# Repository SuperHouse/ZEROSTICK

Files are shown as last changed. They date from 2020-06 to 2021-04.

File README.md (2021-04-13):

"ZeroStick" Zero-Deflection Assistive Technology Joystick
==========================================================

ZeroStick is a joystick that uses strain gauges to measure force
applied to it, without the joystick needing to move. The joystick
"position" is determined from the force being applied to it, instead of
any physical deflection of the stick.

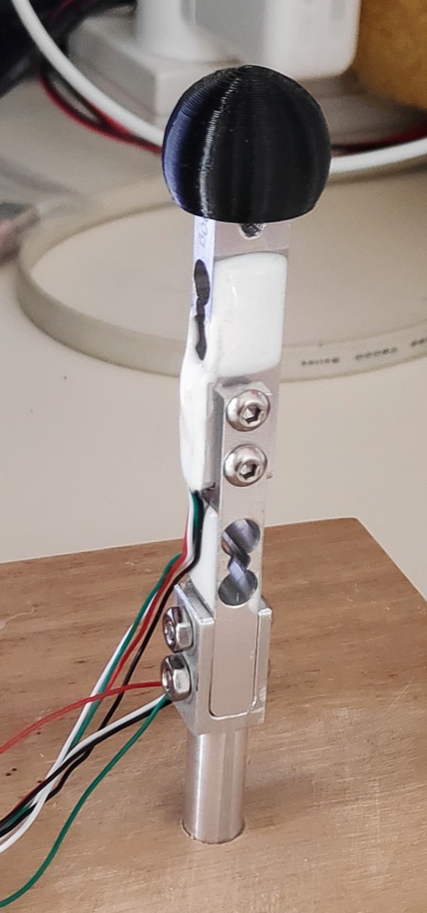
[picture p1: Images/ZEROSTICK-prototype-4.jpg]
ZeroStick Joystick


The term "position" is used here to signify the virtual position of the
joystick, even though it doesn't physically move. As more force is
applied, the virtual position of the joystick is considered to change.

This allows it to be used by people with a limited range of motion,
such as from Duchenne muscular dystrophy.

The sensitivity of the joystick can be adjusted in software by changing
the scaling of the values detected by the strain gauges.

The position value is measured as % deflection from the zero (central)
position, ie: from -100% to +100%. This is equivalent to full effort by
the user in each direction.

The force applied to the load cells is measured using a NAU7802 ADC
with an I2C interface. The input channels are split so that a single
ADC can read both the X and the Y axis load cells sequentially.

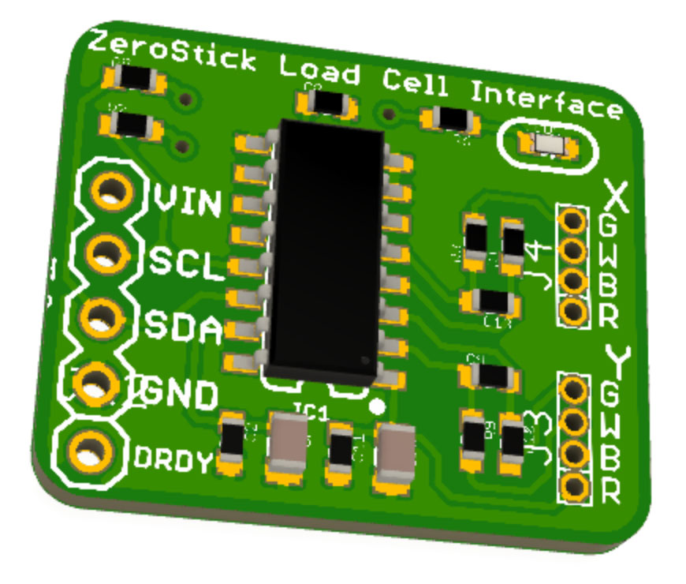
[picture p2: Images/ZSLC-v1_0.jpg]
ZeroStick Load Cell Interface PCB


You can view more details at:

  http://www.superhouse.tv/zerostick

Hardware
--------
The "Hardware" directory contains the PCB design as an EAGLE project.
EAGLE PCB design software is available from Autodesk free for
non-commercial use.

Firmware
--------
The "Firmware" directory contains example firmware as an Arduino
project.

The example firmware has three output methods:

1. Mouse output. When enabled and plugged into a computer, the ZeroStick
will emulate a USB mouse. Buttons on the ZeroStick can also send left
and right click events.

2. Joystick output. When enabled and plugged into a computer, the
ZeroStick will emulate a USB game controller with a joystick.

3. I2C digital potentiometer output. External I2C digital potentiometers
can be connected, which can then emulate a simple analog joystick
when connected to another device such as a wheelchair. This allows the
ZeroStick to control wheelchairs that expect to have a normal joystick
attached.

Credits
-------
  * Jonathan Oxer <jon@oxer.com.au>
  * Chris Fryer <chris.fryer78@gmail.com>

License
-------
Copyright 2019-2021 SuperHouse Automation Pty Ltd  www.superhouse.tv  

The hardware portion of this project is licensed under the TAPR Open
Hardware License (www.tapr.org/OHL). The "license" folder within this
repository contains a copy of this license in plain text format.

The software portion of this project is licensed under the Simplified
BSD License. The "licence" folder within this project contains a
copy of this license in plain text format.

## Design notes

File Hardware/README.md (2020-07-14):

SuperButton Assistive Technology Button
=======================================
Copyright 2020 SuperHouse Automation Pty Ltd <www.superhouse.tv>  
Designed by Jonathan Oxer

Load-cell based button that can have the required activation force
adjusted in software, to tune it based on the needs of the user.

PCB render

Features:

 * 1 x input connection for a load-cell based button
 * 1 x USB connection for power or to emulate an input device
 * 1 x switched output (either N.O. or N.C.) to control other devices
 * 128x32 OLED to show current force reading and activation threshold
 * Rotary encoder to adjust activation threshold
 * "Tare" button to reset zero point
 * Pulse stretching feature controlled by slide switch

More information is available at:

  http://www.superhouse.tv/sb

INSTALLATION
------------
The design is saved as an EAGLE project. EAGLE PCB design software is
available from www.cadsoftusa.com free for non-commercial use. To use
this project download it and place the directory containing these files
into the "eagle" directory on your computer. Then open EAGLE and
navigate to the project.

DISTRIBUTION
------------
The specific terms of distribution of this project are governed by the
license referenced below.

LICENSE
-------
Licensed under the TAPR Open Hardware License (www.tapr.org/OHL).
The "license" folder within this repository also contains a copy of
this license in plain text format.

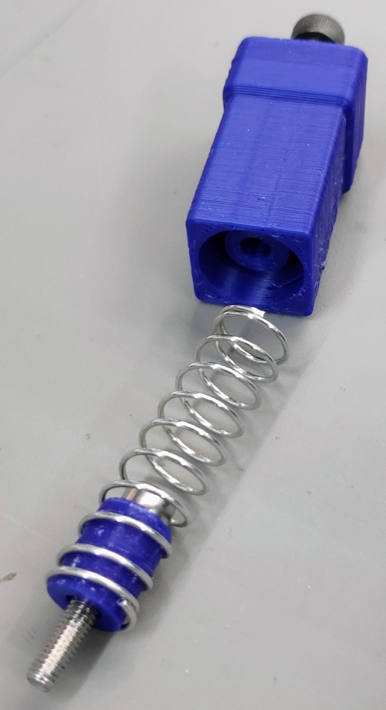
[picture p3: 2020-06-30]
Images/2020-01-04 17.47.43.jpg

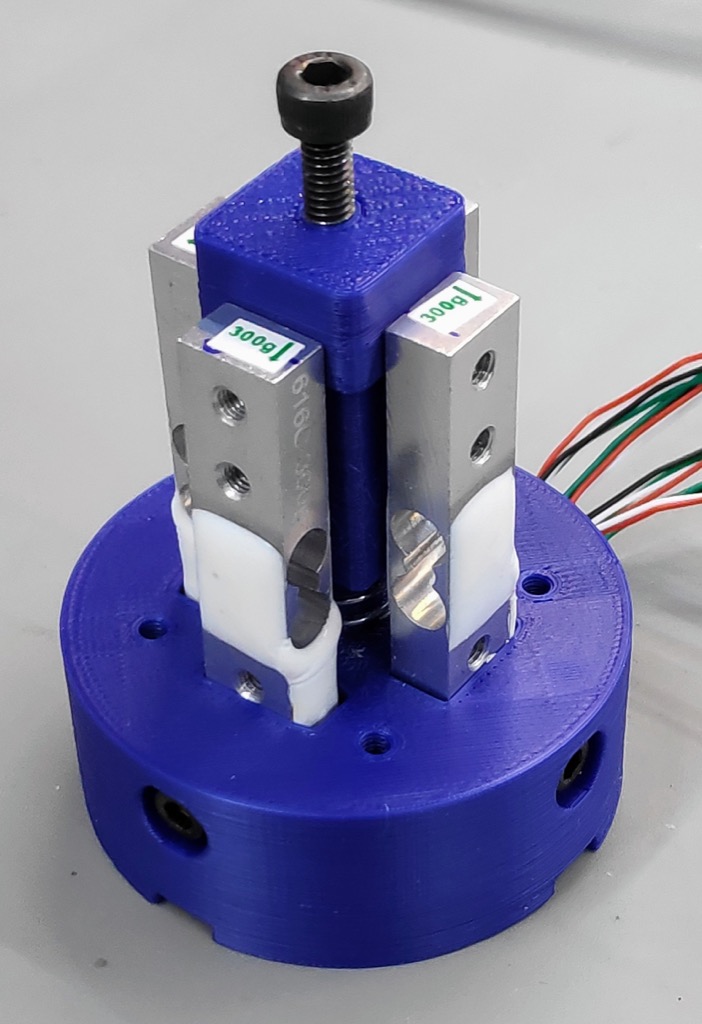
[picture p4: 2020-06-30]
Images/2020-01-04 17.36.29.jpg

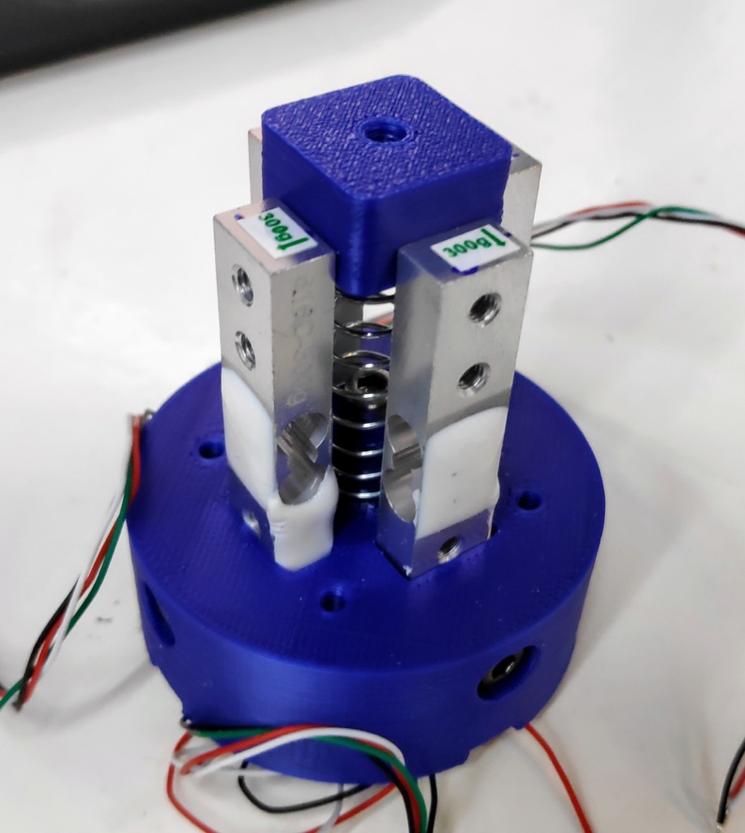
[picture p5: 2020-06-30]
Images/2020-01-04 15.48.38.jpg

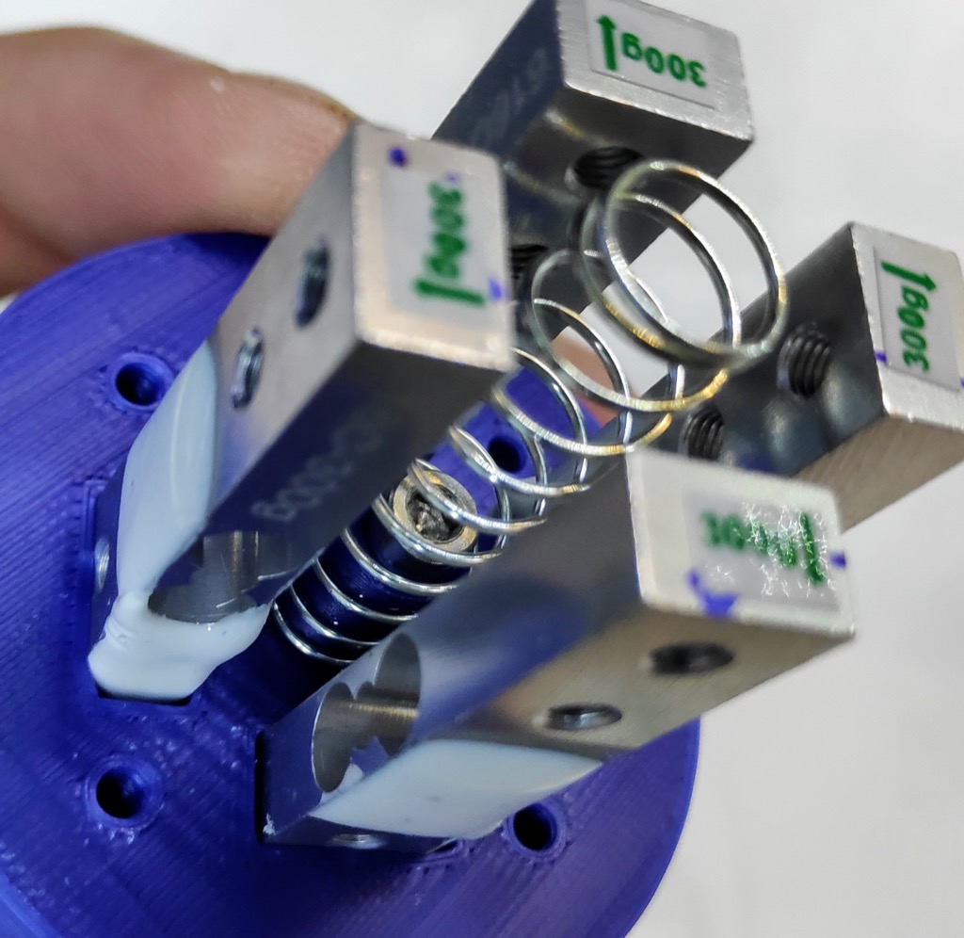
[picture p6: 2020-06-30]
Images/2020-01-04 14.36.33.jpg

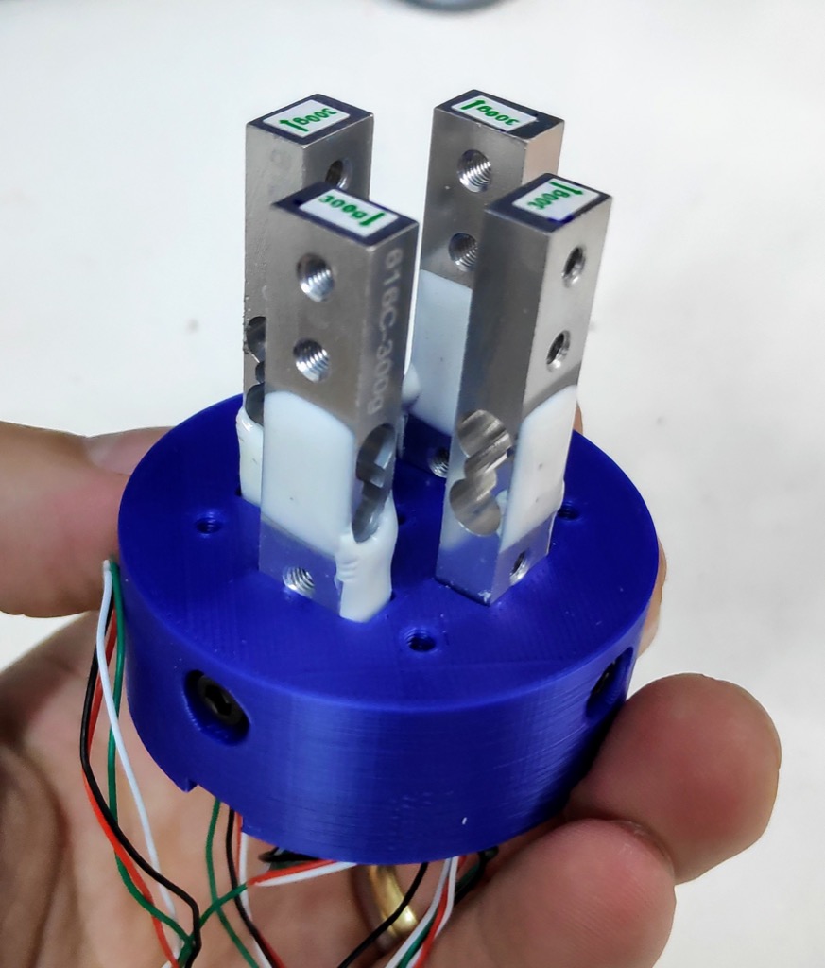
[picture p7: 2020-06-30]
Images/2020-01-04 13.35.04.jpg

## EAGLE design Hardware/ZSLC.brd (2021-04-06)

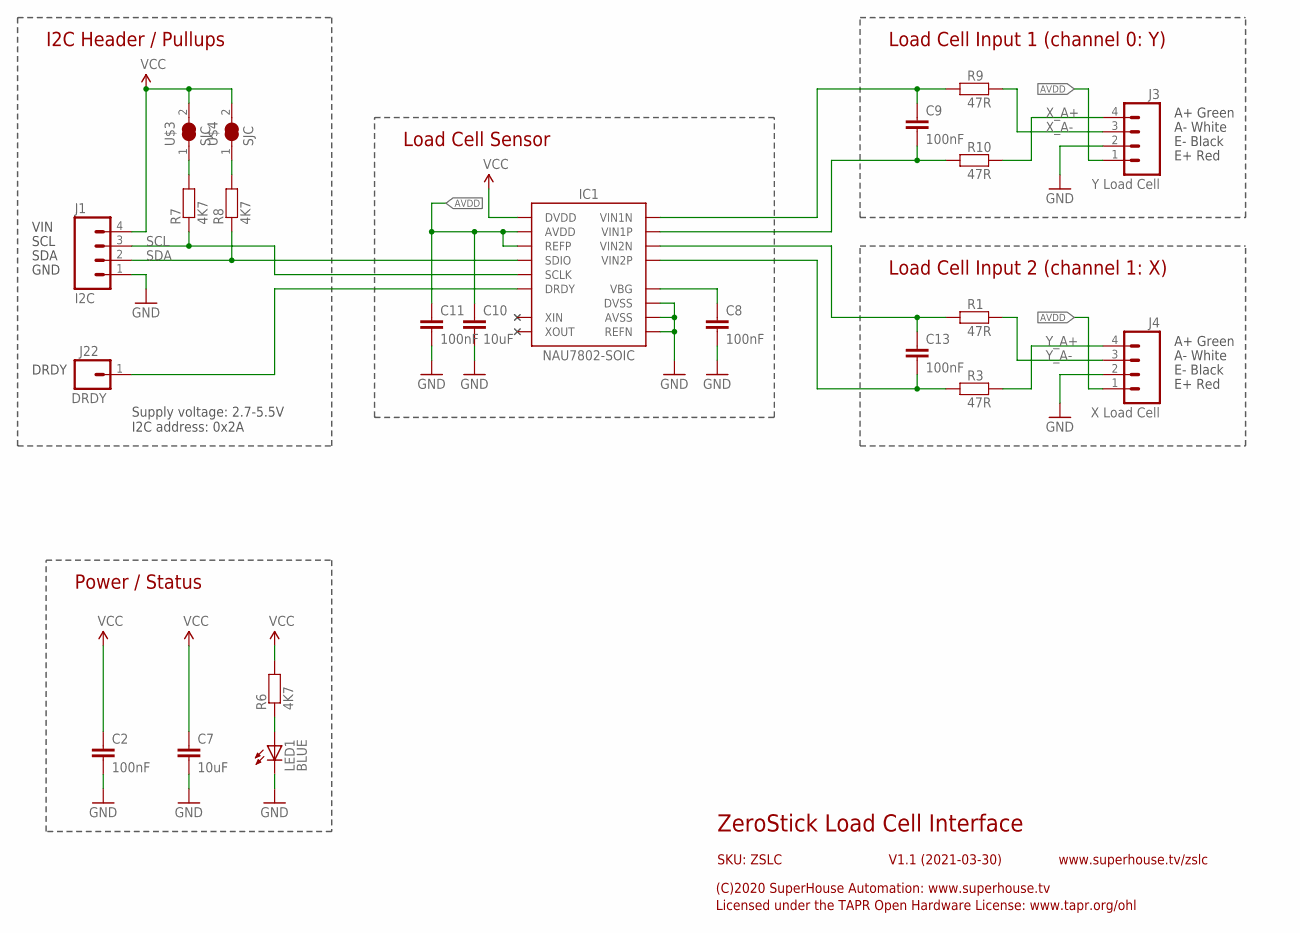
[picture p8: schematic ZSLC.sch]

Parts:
C2, C8, C9, C11, C13: 100nF; C0603
C7, C10: 10uF; C0805
IC1: NAU7802-SOIC; SO16
J1: I2C; 1X04
J3: Y Load Cell; 1X04-1.27-PLAIN
J4: X Load Cell; 1X04-1.27-PLAIN
J22: DRDY; 1X01
LED1: BLUE; LED-0603
R1, R3, R9, R10: 47R; R0603
R6, R7, R8: 4K7; R0603
U$3, U$4: SJC

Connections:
AVDD: C10.1, C11.1, IC1.1 (REFP), IC1.16 (AVDD), J3.1, J4.1
GND: C2.2, C7.2, C8.2, C10.2, C11.2, IC1.7 (REFN), IC1.8 (AVSS), IC1.9 (DVSS), J1.1, J3.2, J4.2, LED1.C
unnamed: IC1.12 (DRDY), J22.1
unnamed: C13.1, IC1.4 (VIN2N), R1.1
unnamed: C13.2, IC1.5 (VIN2P), R3.1
unnamed: LED1.A, R6.1
unnamed: C9.1, IC1.2 (VIN1N), R9.1
unnamed: C9.2, IC1.3 (VIN1P), R10.1
unnamed: C8.1, IC1.6 (VBG)
unnamed: R7.2, U$3.1
unnamed: R8.2, U$4.1
SCL: IC1.13 (SCLK), J1.3, R7.1
SDA: IC1.14 (SDIO), J1.2, R8.1
VCC: C2.1, C7.1, IC1.15 (DVDD), J1.4, R6.2, U$3.2, U$4.2
X_A+: J3.4, R10.2
X_A-: J3.3, R9.2
Y_A+: J4.4, R3.2
Y_A-: J4.3, R1.2

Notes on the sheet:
ZeroStick Load Cell Interface
V1.1 (2021-03-30)
SKU: ZSLC
(C)2020 SuperHouse Automation: www.superhouse.tv
Licensed under the TAPR Open Hardware License: www.tapr.org/ohl
www.superhouse.tv/zslc
Power / Status
Load Cell Input 1 (channel 0: Y)
Load Cell Input 2 (channel 1: X)
I2C Header / Pullups
E+ Red
E- Black
A- White
A+ Green
Supply voltage: 2.7-5.5V I2C address: 0x2A
Load Cell Sensor
VIN
SCL
SDA
GND
DRDY

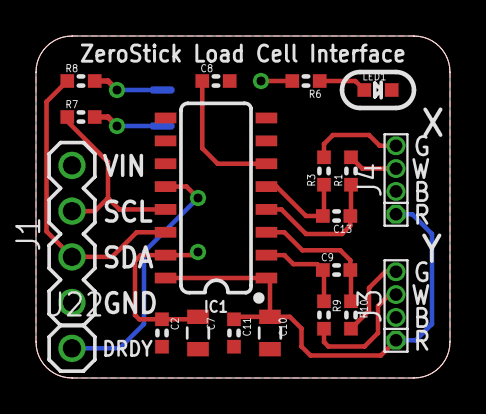
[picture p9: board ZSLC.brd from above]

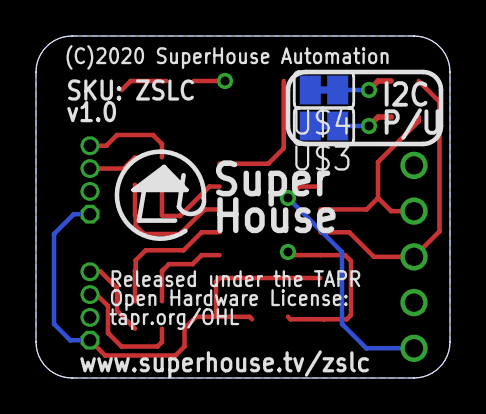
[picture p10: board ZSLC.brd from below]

Board: 2 copper layers, 23.0 x 19.0 mm, 22 parts (2 on the bottom side), 18 nets.

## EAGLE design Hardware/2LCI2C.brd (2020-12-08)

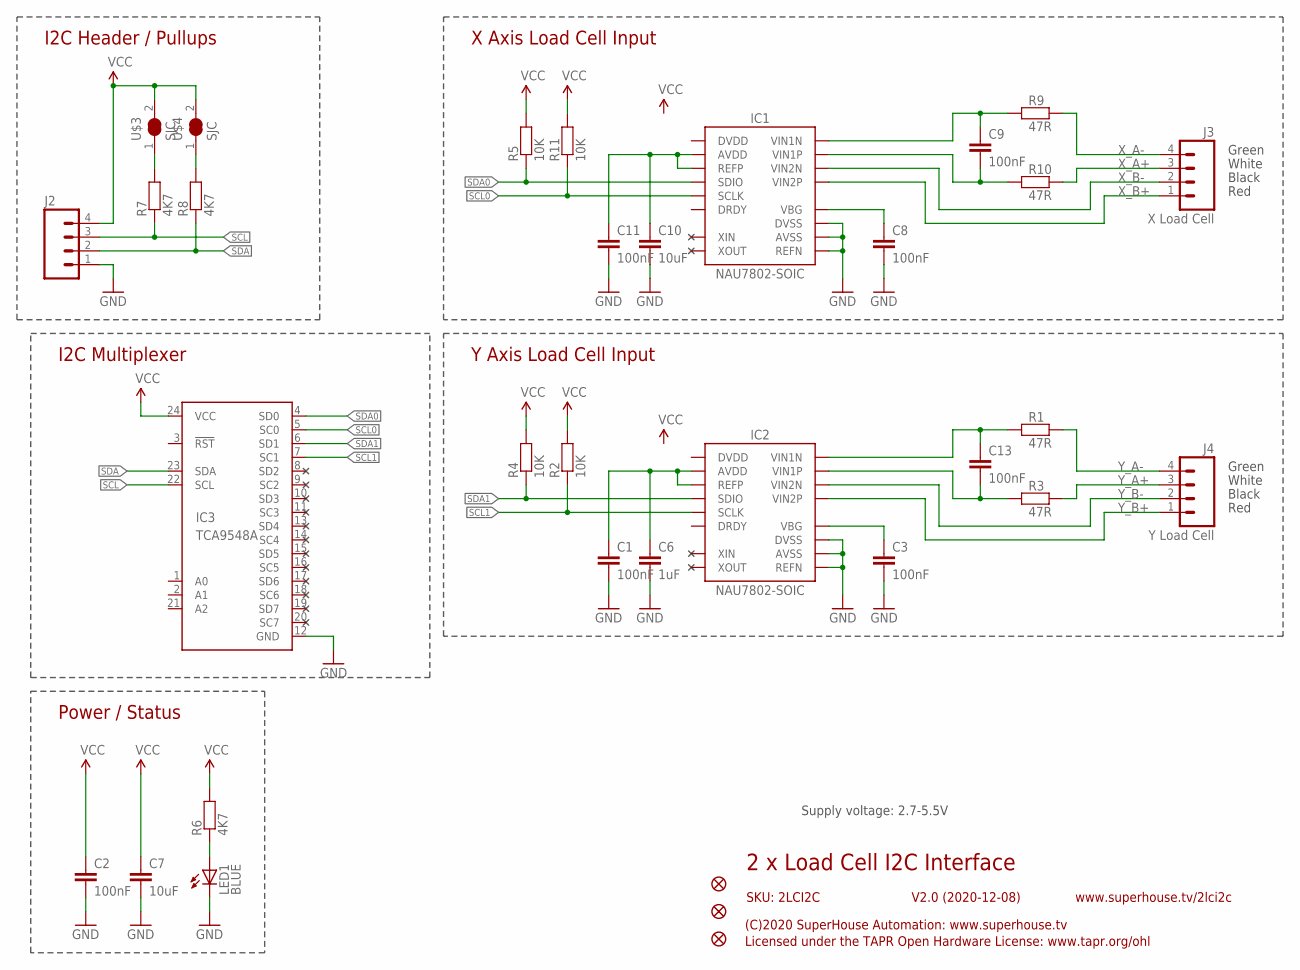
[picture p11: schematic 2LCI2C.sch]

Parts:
C1, C2, C3, C8, C9, C11, C13: 100nF; C0603
C6: 1uF; C0805
C7, C10: 10uF; C0805
IC1, IC2: NAU7802-SOIC; SO16
IC3: TCA9548A; TSSOP24
J2: M04-PLAIN; 1X04
J3: X Load Cell; 1X04-1.27-PLAIN
J4: Y Load Cell; 1X04-1.27-PLAIN
LED1: BLUE; LED-0603
R1, R3, R9, R10: 47R; R0603
R2, R4, R5, R11: 10K; R0603
R6, R7, R8: 4K7; R0603
U$3, U$4: SJC
U$5, U$10, U$11: FIDUCIAL1X2.5; FIDUCIAL-1X2.5

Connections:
GND: C1.2, C2.2, C3.2, C6.2, C7.2, C8.2, C10.2, C11.2, IC1.7 (REFN), IC1.8 (AVSS), IC1.9 (DVSS), IC2.7 (REFN), IC2.8 (AVSS), IC2.9 (DVSS), IC3.12 (GND), J2.1, LED1.C
unnamed: C3.1, IC2.6 (VBG)
unnamed: C13.1, IC2.2 (VIN1N), R1.1
unnamed: C1.1, C6.1, IC2.1 (REFP), IC2.16 (AVDD)
unnamed: C13.2, IC2.3 (VIN1P), R3.1
unnamed: LED1.A, R6.1
unnamed: C9.1, IC1.2 (VIN1N), R9.1
unnamed: C9.2, IC1.3 (VIN1P), R10.1
unnamed: C8.1, IC1.6 (VBG)
unnamed: C10.1, C11.1, IC1.1 (REFP), IC1.16 (AVDD)
unnamed: R7.2, U$3.1
unnamed: R8.2, U$4.1
SCL: IC3.22 (SCL), J2.3, R7.1
SCL0: IC1.13 (SCLK), IC3.5 (SC0), R11.1
SCL1: IC2.13 (SCLK), IC3.7 (SC1), R2.1
SDA: IC3.23 (SDA), J2.2, R8.1
SDA0: IC1.14 (SDIO), IC3.4 (SD0), R5.1
SDA1: IC2.14 (SDIO), IC3.6 (SD1), R4.1
VCC: C2.1, C7.1, IC3.24 (VCC), J2.4, R2.2, R4.2, R5.2, R6.2, R11.2, U$3.2, U$4.2
X_A+: J3.3, R10.2
X_A-: J3.4, R9.2
X_B+: IC1.5 (VIN2P), J3.1
X_B-: IC1.4 (VIN2N), J3.2
Y_A+: J4.3, R3.2
Y_A-: J4.4, R1.2
Y_B+: IC2.5 (VIN2P), J4.1
Y_B-: IC2.4 (VIN2N), J4.2

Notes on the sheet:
2 x Load Cell I2C Interface
V2.0 (2020-12-08)
SKU: 2LCI2C
(C)2020 SuperHouse Automation: www.superhouse.tv
Licensed under the TAPR Open Hardware License: www.tapr.org/ohl
www.superhouse.tv/2lci2c
Power / Status
X Axis Load Cell Input
Y Axis Load Cell Input
I2C Header / Pullups
I2C Multiplexer
Red
Black
White
Green
Supply voltage: 2.7-5.5V

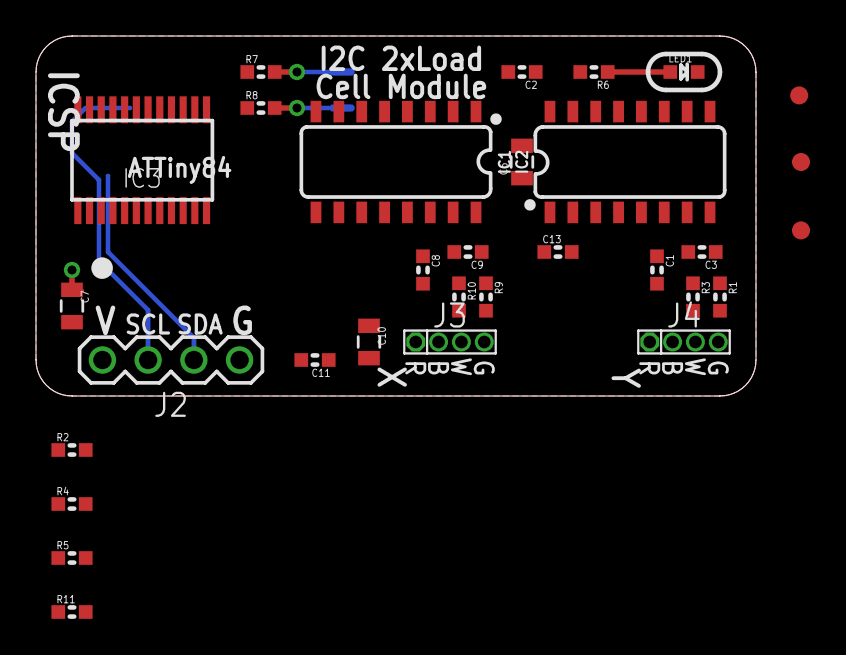
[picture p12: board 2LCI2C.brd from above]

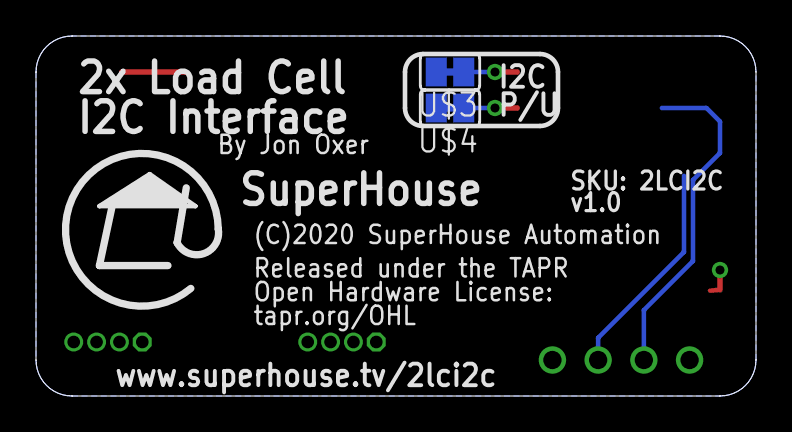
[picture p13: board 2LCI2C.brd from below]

Board: 2 copper layers, 40.0 x 20.0 mm, 33 parts (2 on the bottom side), 27 nets.

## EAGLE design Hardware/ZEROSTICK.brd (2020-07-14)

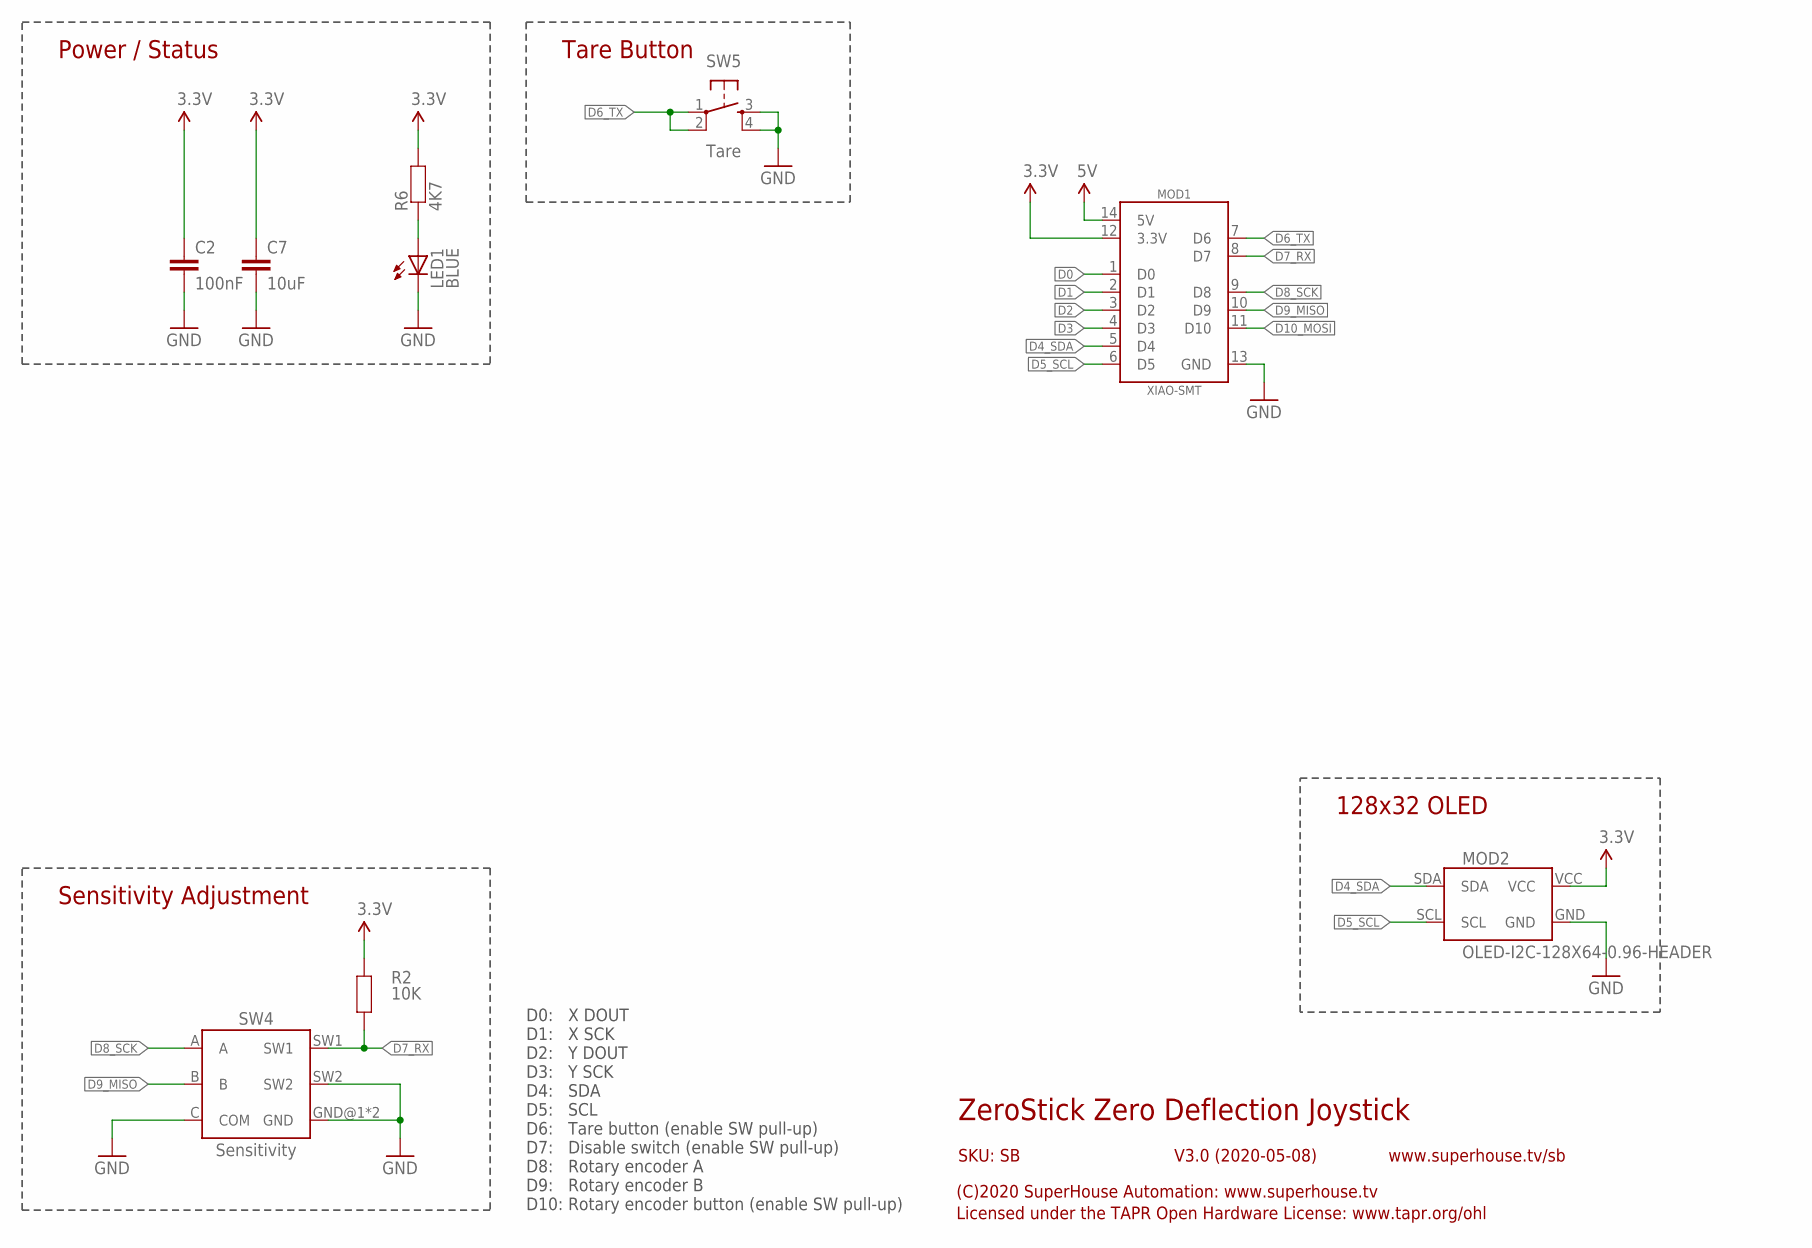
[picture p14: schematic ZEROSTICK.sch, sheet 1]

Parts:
C2: 100nF; C0603
C7: 10uF; C0805
LED1: BLUE; LED-0603
MOD1: XIAO-SMT
MOD2: OLED-I2C-128X64-0.96-HEADER; OLED-128X64-0.96-HEADER
R2: 10K; R0603
R6: 4K7; R0603
SW4: Sensitivity; PEC12R
SW5: Tare; TACTILE-PTH-4.5MM

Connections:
3.3V: C2.1, C7.1, MOD1.12 (3.3V), MOD2.VCC, R2.2, R6.2; also elsewhere on the board
5V: MOD1.14 (5V)
D0: MOD1.1 (D0); also elsewhere on the board
D1: MOD1.2 (D1); also elsewhere on the board
D2: MOD1.3 (D2); also elsewhere on the board
D3: MOD1.4 (D3); also elsewhere on the board
D4_SDA: MOD1.5 (D4), MOD2.SDA
D5_SCL: MOD1.6 (D5), MOD2.SCL
D6_TX: MOD1.7 (D6), SW5.1, SW5.2
D7_RX: MOD1.8 (D7), R2.1, SW4.SW1
D8_SCK: MOD1.9 (D8), SW4.A
D9_MISO: MOD1.10 (D9), SW4.B
D10_MOSI: MOD1.11 (D10)
GND: C2.2, C7.2, LED1.C, MOD1.13 (GND), MOD2.GND, SW4.C (COM), SW4.GND@1 (GND), SW4.GND@2 (GND), SW4.SW2, SW5.3, SW5.4; also elsewhere on the board
unnamed: LED1.A, R6.1

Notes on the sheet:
Tare Button
ZeroStick Zero Deflection Joystick
V3.0 (2020-05-08)
SKU: SB
(C)2020 SuperHouse Automation: www.superhouse.tv
Licensed under the TAPR Open Hardware License: www.tapr.org/ohl
www.superhouse.tv/sb
Power / Status
Sensitivity Adjustment
128x32 OLED
D0: X DOUT D1: X SCK D2: Y DOUT D3: Y SCK D4: SDA D5: SCL D6: Tare button (enable SW pull-up) D7: Disable switch (enable SW pull-up) D8: Rotary encoder A D9: Rotary encoder B D10: Rotary encoder button (enable SW pull-up)

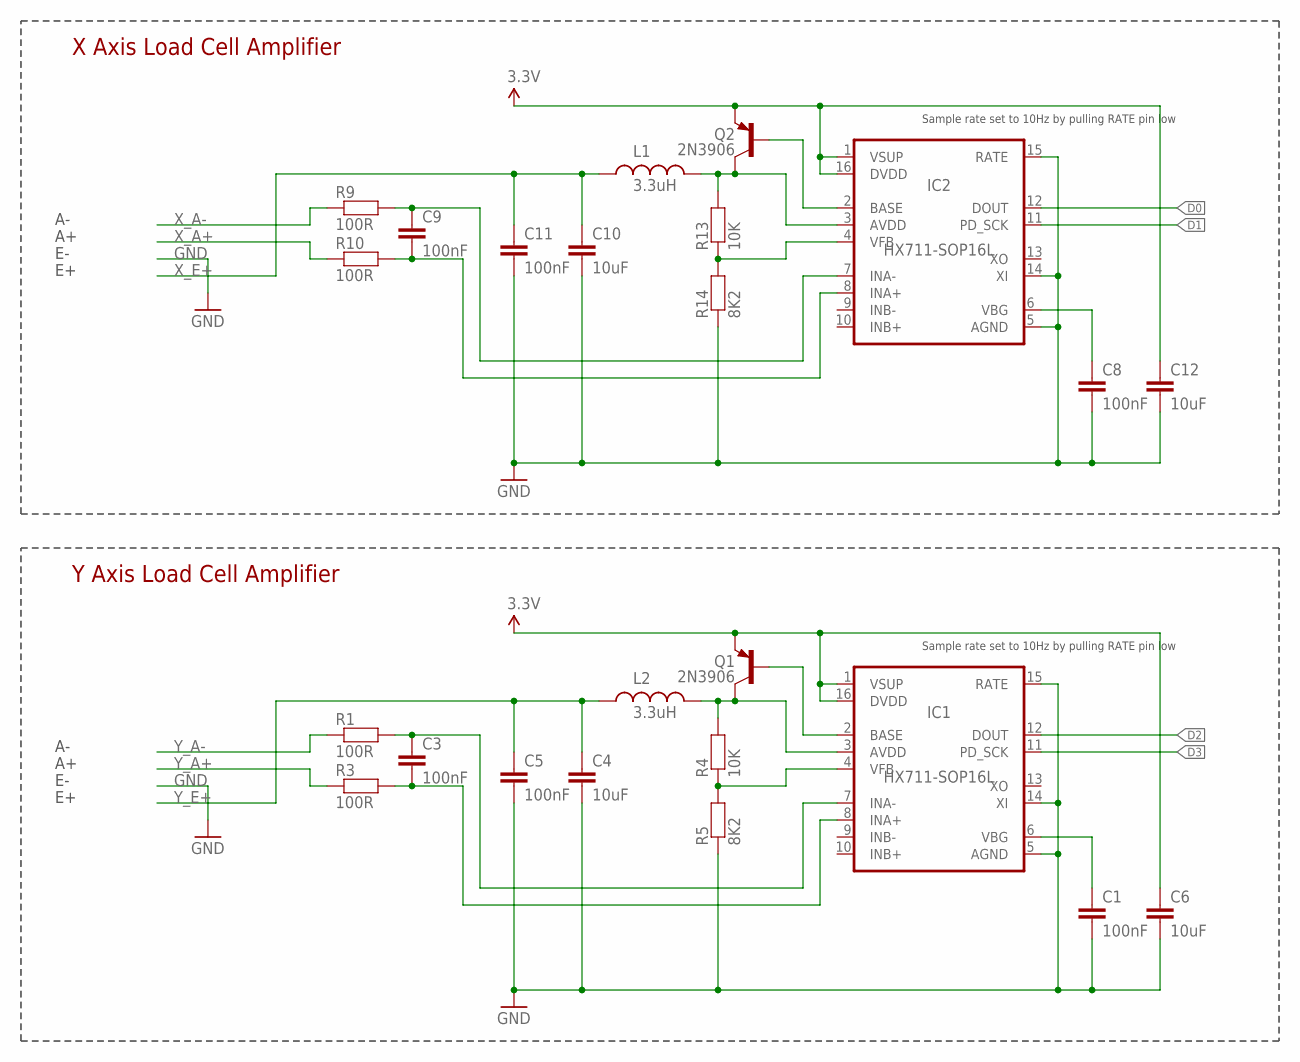
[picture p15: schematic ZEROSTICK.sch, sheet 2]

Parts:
C1, C3, C5, C8, C9, C11: 100nF; C0603
C4, C6, C10, C12: 10uF; C0805
IC1, IC2: HX711-SOP16L; SOP16-L
L1, L2: 3.3uH; L0603
Q1, Q2: 2N3906; SOT23-BEC
R1, R3, R9, R10: 100R; R0603
R4, R13: 10K; R0603
R5, R14: 8K2; R0603

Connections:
3.3V: C6.1, C12.1, IC1.1 (VSUP), IC1.16 (DVDD), IC2.1 (VSUP), IC2.16 (DVDD), Q1.E, Q2.E; also elsewhere on the board
D0: IC2.12 (DOUT); also elsewhere on the board
D1: IC2.11 (PD_SCK); also elsewhere on the board
D2: IC1.12 (DOUT); also elsewhere on the board
D3: IC1.11 (PD_SCK); also elsewhere on the board
GND: C1.2, C4.2, C5.2, C6.2, C8.2, C10.2, C11.2, C12.2, IC1.5 (AGND), IC1.14 (XI), IC1.15 (RATE), IC2.5 (AGND), IC2.14 (XI), IC2.15 (RATE), R5.1, R14.1; also elsewhere on the board
unnamed: C3.1, IC1.7 (INA-), R1.2
unnamed: C3.2, IC1.8 (INA+), R3.2
unnamed: C1.1, IC1.6 (VBG)
unnamed: IC1.2 (BASE), Q1.B
unnamed: IC1.4 (VFB), R4.1, R5.2
unnamed: IC1.3 (AVDD), L2.2, Q1.C, R4.2
unnamed: C9.1, IC2.7 (INA-), R9.2
unnamed: C9.2, IC2.8 (INA+), R10.2
unnamed: IC2.3 (AVDD), L1.2, Q2.C, R13.2
unnamed: C8.1, IC2.6 (VBG)
unnamed: IC2.2 (BASE), Q2.B
unnamed: IC2.4 (VFB), R13.1, R14.2
XO: IC1.13 (XO), IC2.13 (XO)
X_A+: R10.1
X_A-: R9.1
X_E+: C10.1, C11.1, L1.1
Y_A+: R3.1
Y_A-: R1.1
Y_E+: C4.1, C5.1, L2.1

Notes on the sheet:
X Axis Load Cell Amplifier
Sample rate set to 10Hz by pulling RATE pin low
Y Axis Load Cell Amplifier

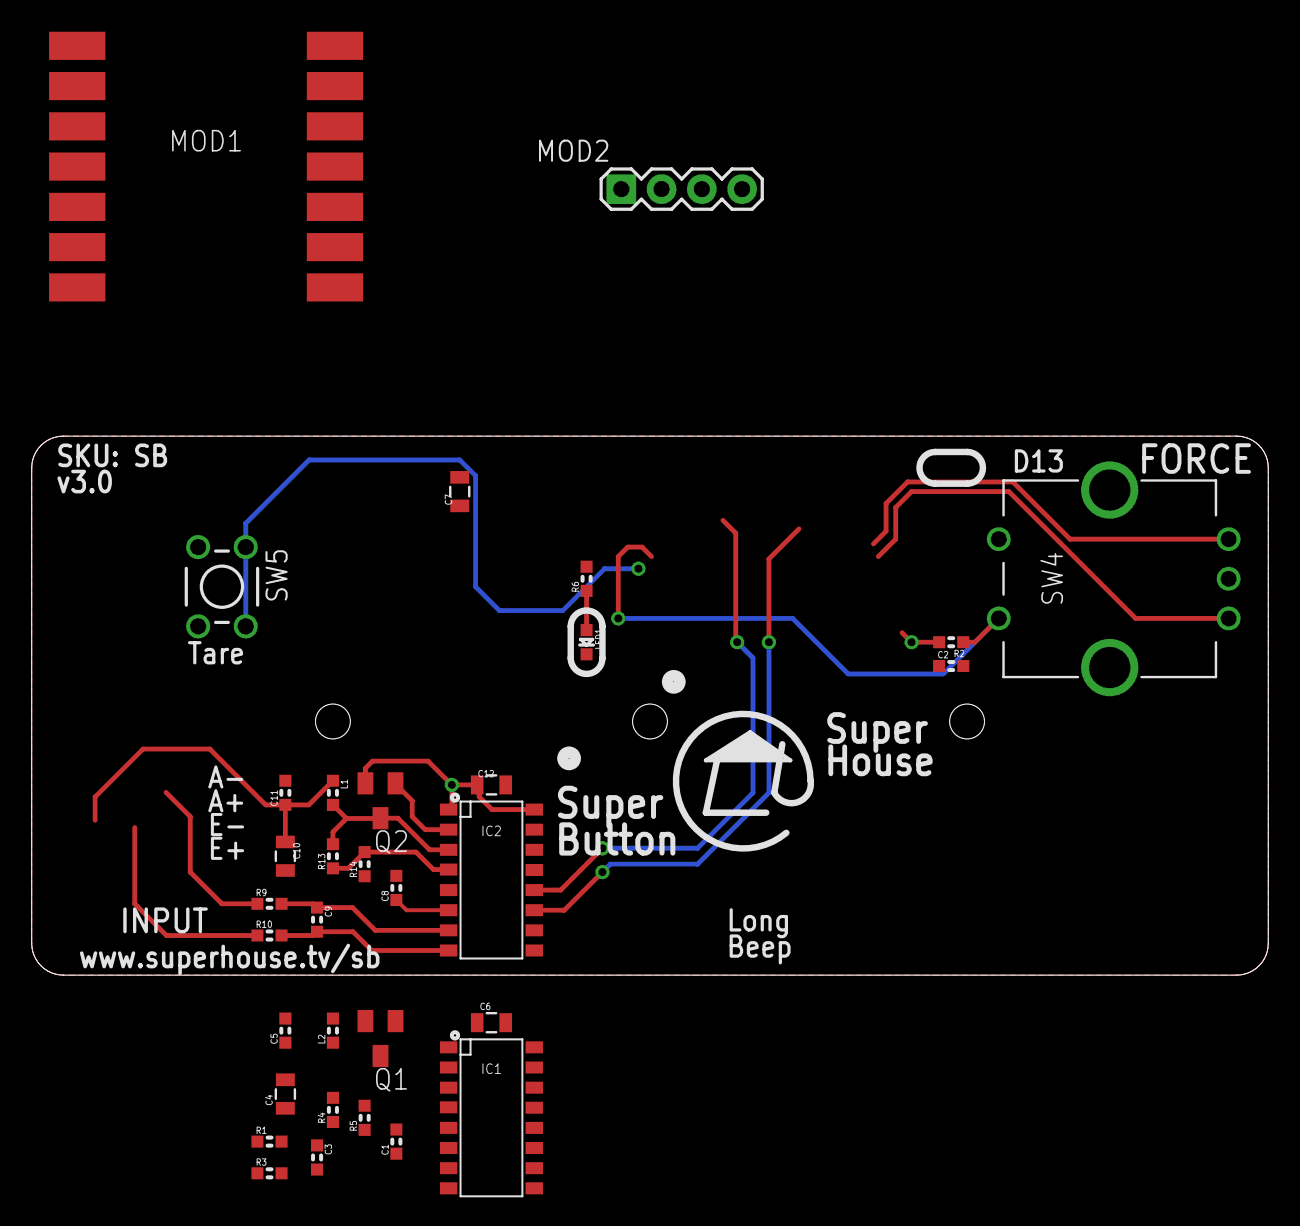
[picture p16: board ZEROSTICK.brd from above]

Board: 2 copper layers, 78.0 x 34.0 mm, 33 parts (0 on the bottom side), 28 nets.

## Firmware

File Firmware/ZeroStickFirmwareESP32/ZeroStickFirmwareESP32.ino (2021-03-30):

/**
   "Zero Deflection" Assistive Technology Joystick

   Uses strain gauges to measure force on a joystick that doesn't
   need to deflect. The joystick output is taken from the force
   applied to it, instead of the physical deflection of the stick.
   This allows it to be used by people with limited range of motion.

   The sensitivity of the joystick can be adjusted in software by
   changing the scaling of the values detected by the strain
   gauges.

   The term "position" is used through the code to signify the
   virtual position of the joystick, even though it doesn't physically
   move. As more force is applied, the virtual position of the
   joystick is considered to change.

   Position is measured as % deflection from the zero (central)
   position, ie: from -100% to +100%. This is equivalent to full
   effort by the user in each direction.

                     Y axis
                     +100%
                       ^
                       |
    X axis   -100% <-- 0 --> +100%
                       |
                       v
                     -100%

   These percentages are scaled to suit different output methods,
   including mouse emulation and joystick emulation.

   Internal dependencies. Install using Arduino library manager:
     "SparkFun Qwiic Scale NAU7802" by SparkFun Electronics
     "Arduino TinyUSB" by Adafruit
     "SoftWire" by Steve Marple
     "AsyncDelay" by Steve Marple

   External dependencies. Install manually:
     "Arduino Joystick Library" by Matthew Heironimus https://github.com/MHeironimus/ArduinoJoystickLibrary

   More information:
     www.superhouse.tv/zerostick

   To do:
    - Does the tare operation act on both inputs, or only the currently
      selected channel?
    - Do we need setZeroOffset() after calculateZeroOffset() in setup?

   Leonardo pin assignments:
     A0:
     A1:
     A2:
     A3:
     A4:
     A5:
     D0:
     D1:
     D2:  SDA
     D3:  SCL
     D4:  LOADCELL_X_SCK_PIN
     D5:  LOADCELL_X_DOUT_PIN
     D6:  LOADCELL_Y_SCK_PIN
     D7:  LOADCELL_Y_DOUT_PIN
     D8:  Disable pin
     D9:
     D10:
     D11:
     D12:
     D13: LED_PIN

   XIAO pin assignments:
     D0:
     D1:
     D2:
     D3:
     D4:  SDA
     D5:  SCL
     D6:  Tare pin
     D7:  Disable pin
     D8:
     D9:
     D10:

   227g (Pocophone) = 920000 reading

   By:
    Chris Fryer <chris.fryer78@gmail.com>
    Jonathan Oxer <jon@oxer.com.au>

   Copyright 2019-2021 SuperHouse Automation Pty Ltd www.superhouse.tv
*/
#define VERSION "2.3"
/*--------------------------- Configuration ---------------------------------*/
// Configuration should be done in the included file:
#include "config.h"

/*--------------------------- Libraries -------------------------------------*/
#include <Wire.h>
#include "SparkFun_Qwiic_Scale_NAU7802_Arduino_Library.h" // Load cell amplifier

/*--------------------------- Global Variables ------------------------------*/
//int16_t  g_zero_tare_offset_x    = 0;   // X axis tare correction
//int16_t  g_zero_tare_offset_y    = 0;   // Y axis tare correction

int32_t   g_input_x_position      = 0;   // Most recent force reading from X axis (+/- %)
int32_t   g_input_y_position      = 0;   // Most recent force reading from Y axis (+/- %)

uint32_t g_last_mouse_time       = 0;   // When we last sent a mouse event
uint32_t g_last_joystick_time    = 0;   // When we last sent a joystick event
uint32_t g_last_digipot_time     = 0;   // When we last updated the digipot outputs

uint8_t  g_left_button_state     = 0;
uint8_t  g_right_button_state    = 0;

float    g_x_calibration_factor  = 1.0;
float    g_y_calibration_factor  = 1.0;
int32_t  g_x_zero_offset         = 0;
int32_t  g_y_zero_offset         = 0;
uint8_t  g_next_axis_to_read     = 0;   // 0 = X axis, 1 = Y axis
uint8_t  g_channel_read_count    = 0;   // Accumulate how many times channel has been read
int32_t  g_sensor_raw_value_sum  = 0;   // Accumulate channel readings

/*--------------------------- Function Signatures ---------------------------*/
/*
  void     readInputPosition();
  int16_t  getScaledLoadCellValueX();
  int16_t  getScaledLoadCellValueY(); */

/*--------------------------- Instantiate Global Objects --------------------*/
// Load cells
NAU7802 loadcell_x;
NAU7802 loadcell_y;

/*--------------------------- Program ---------------------------------------*/
/**
  Setup
*/
void setup()
{
  Serial.begin(SERIAL_BAUD_RATE);
  delay(1000);
  //while (!Serial) {
  //  ; // wait for serial port to connect. Needed for native USB port only
  //}
  //Serial.print("ZeroStick starting up, v");
  //Serial.println(VERSION);

  pinMode(I2C_X_SDA_PIN, INPUT_PULLUP);
  pinMode(I2C_X_SCL_PIN, INPUT_PULLUP);


  //Wire.begin();
  Wire.begin(I2C_Y_SDA_PIN, I2C_Y_SCL_PIN); //uses default SDA and SCL and 100000HZ freq
  //Wire1.begin(I2C_X_SDA_PIN, I2C_X_SCL_PIN, 100000);
  Wire1.begin(I2C_X_SDA_PIN, I2C_X_SCL_PIN);

  pinMode(DISABLE_PIN,            INPUT_PULLUP);
  pinMode(TARE_BUTTON_PIN,        INPUT_PULLUP);
  pinMode(MOUSE_LEFT_BUTTON_PIN,  INPUT_PULLUP);
  pinMode(MOUSE_RIGHT_BUTTON_PIN, INPUT_PULLUP);

  // Start the X-axis load cell interface
  //Serial.print("Starting X-axis load cell interface: ");
  if (loadcell_x.begin(Wire1) == false)
  {
    Serial.println("X-axis load cell not detected. Halting.");
    while (1);
  }
  //Serial.println("ok.");
  loadcell_x.setGain(NAU7802_GAIN_64);        // Gain can be set to 1, 2, 4, 8, 16, 32, 64, or 128.
  loadcell_x.setSampleRate(NAU7802_SPS_80); // Sample rate can be set to 10, 20, 40, 80, or 320Hz

  // Start the Y-axis load cell interface
  //Serial.print("Starting Y-axis load cell interface: ");
  if (loadcell_y.begin(Wire) == false)
  {
    Serial.println("Y-axis load cell not detected. Halting.");
    while (1);
  }
  //Serial.println("ok.");
  loadcell_y.setGain(NAU7802_GAIN_64);        // Gain can be set to 1, 2, 4, 8, 16, 32, 64, or 128.
  loadcell_y.setSampleRate(NAU7802_SPS_80); // Sample rate can be set to 10, 20, 40, 80, or 320Hz

  delay(100);


  tareCellReadings();
}

/**
  Loop
*/
void loop()
{
  //Serial.println(millis());
  checkTareButton();
  checkMouseButtons();

  readInputPosition();

  //updateMouseOutput();
  //updateJoystickOutput();
  //updateDigipotOutputs();
}

/**
  Check if the tare button is pressed
*/
void checkTareButton()
{
  if (LOW == digitalRead(TARE_BUTTON_PIN))
  {
    // Button is pressed, do the tare!
    delay(100);
    tareCellReadings();
    delay(100);
  }
}


/**

*/
void checkMouseButtons()
{
  uint8_t left_button_state = digitalRead(MOUSE_LEFT_BUTTON_PIN);
  if (LOW == left_button_state)
  {
    if (HIGH == g_left_button_state)
    {
      Serial.println("press");
      g_left_button_state = LOW;
    }
  }
  if (HIGH == left_button_state)
  {
    if (LOW == g_left_button_state)
    {
      Serial.println("up");
      g_left_button_state = HIGH;
    }
  }

  uint8_t right_button_state = digitalRead(MOUSE_RIGHT_BUTTON_PIN);
  if (LOW == right_button_state)
  {
    if (HIGH == g_right_button_state)
    {
      Serial.println("down");
      g_right_button_state = LOW;
    }
  }
  if (HIGH == right_button_state)
  {
    if (LOW == g_right_button_state)
    {
      Serial.println("up");
      g_right_button_state = HIGH;
    }
  }
}


/**
  Read the sensor pressure levels
*/
void readInputPosition()
{
  if (0 == g_next_axis_to_read) // X axis
  {
    if (loadcell_x.available() == true)
    {
      g_sensor_raw_value_sum += loadcell_x.getReading();
      g_channel_read_count++;

      if (SAMPLE_COUNT == g_channel_read_count)
      {
        g_input_x_position = (g_sensor_raw_value_sum / SAMPLE_COUNT);

        /*
          int32_t sensor_raw_value = (g_sensor_raw_value_sum / SAMPLE_COUNT) - g_x_zero_offset;
          //Serial.println(sensor_raw_value);
          //Serial.print("X: ");
          //Serial.println(sensor_raw_value);
          g_input_x_position = sensor_raw_value;
          //g_input_x_position = (int8_t)map(sensor_raw_value, -10000, 10000, -100, 100); // Adjust to a percentage of full force
          //g_input_x_position = constrain(g_input_x_position, -100, 100);          // Prevent going out of bounds

          if (INPUT_DEAD_SPOT_SIZE < g_input_x_position)
          {
          g_input_x_position -= INPUT_DEAD_SPOT_SIZE;
          } else if (-1 * INPUT_DEAD_SPOT_SIZE > g_input_x_position) {
          g_input_x_position += INPUT_DEAD_SPOT_SIZE;
          } else {
          g_input_x_position = 0;
          }
        */

        g_channel_read_count   = 0;
        g_sensor_raw_value_sum = 0;
        g_next_axis_to_read = 1;
        //loadcell_x.setChannel(1);
        //loadcell_x.calibrateAFE();
      }
    }
  }
  if (1 == g_next_axis_to_read) // Y axis
  {
    if (loadcell_y.available() == true)
    {
      //Serial.println("Reading Y");
      g_sensor_raw_value_sum += loadcell_y.getReading();
      g_channel_read_count++;

      if (SAMPLE_COUNT == g_channel_read_count)
      {
        g_input_y_position = (g_sensor_raw_value_sum / SAMPLE_COUNT);

        /*
          int32_t sensor_raw_value = (g_sensor_raw_value_sum / SAMPLE_COUNT) - g_y_zero_offset;
          sensor_raw_value = (int)sensor_raw_value * Y_SCALING_FACTOR;
          //Serial.print("           Y:");
          //Serial.println(sensor_raw_value);
          g_input_y_position = sensor_raw_value;
          //g_input_y_position = (int8_t)map(sensor_raw_value, -10000, 10000, -100, 100); // Adjust to a percentage of full force
          //g_input_y_position = constrain(g_input_y_position, -100, 100);          // Prevent going out of bounds

          if (INPUT_DEAD_SPOT_SIZE < g_input_y_position)
          {
          g_input_y_position -= INPUT_DEAD_SPOT_SIZE;
          } else if (-1 * INPUT_DEAD_SPOT_SIZE > g_input_y_position) {
          g_input_y_position += INPUT_DEAD_SPOT_SIZE;
          } else {
          g_input_y_position = 0;
          }
        */

        g_channel_read_count   = 0;
        g_sensor_raw_value_sum = 0;
        g_next_axis_to_read = 0;
        //loadcell_x.setChannel(1);
        //loadcell_x.calibrateAFE();
      }
    }
  }

#if ENABLE_SERIAL_DEBUGGING2
  Serial.print(g_input_x_position);
  Serial.print("  ");
  Serial.println(g_input_y_position);
#endif

}

/**
  Reset the zero position of the load cells. Select each channel in turn and tare them.
*/
void tareCellReadings()
{
  loadcell_x.setChannel(1);
  loadcell_x.calibrateAFE();                 // Internal calibration. Recommended after power up, gain changes, sample rate changes, or channel changes.
  loadcell_x.calculateZeroOffset(64);        // Tare operation, averaged across 64 readings
  loadcell_x.setCalibrationFactor(g_x_calibration_factor);
  g_x_zero_offset = loadcell_x.getZeroOffset();
#if ENABLE_SERIAL_DEBUGGING
  Serial.println("\n-----------");
  Serial.print("X zero offset: ");
  Serial.println(loadcell_x.getZeroOffset());
  Serial.print("X calibration factor: ");
  Serial.println(loadcell_x.getCalibrationFactor());
#endif

  loadcell_y.setChannel(1);
  loadcell_y.calibrateAFE();                 // Internal calibration. Recommended after power up, gain changes, sample rate changes, or channel changes.
  loadcell_y.calculateZeroOffset(64);        // Tare operation, averaged across 64 readings
  loadcell_y.setCalibrationFactor(g_y_calibration_factor);
  g_y_zero_offset = loadcell_y.getZeroOffset();
#if ENABLE_SERIAL_DEBUGGING
  Serial.print("Y zero offset: ");
  Serial.println(loadcell_y.getZeroOffset());
  Serial.print("Y calibration factor: ");
  Serial.println(loadcell_y.getCalibrationFactor());
  Serial.println("-----------");
#endif

  //loadcell_x.setChannel(g_next_axis_to_read); // To leave the selected channel in the correct state

#if ENABLE_SERIAL_DEBUGGING
  Serial.println("Tare complete");
#endif
}

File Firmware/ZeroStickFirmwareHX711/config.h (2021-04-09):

/* ----------------- General config -------------------------------- */
/* Output options */
#define   ENABLE_SERIAL_DEBUGGING true
#define   ENABLE_DIGIPOT_OUTPUT   false
#define   ENABLE_MOUSE_OUTPUT     true
#define   ENABLE_JOYSTICK_OUTPUT  false

/* Input behaviour */
#define   INPUT_DEAD_SPOT_SIZE        2  // +/- this % will be ignored

/* Mouse behaviour */
// 0.1 is super slow. 1.0 is really fast. 0.5 is generally ok.
#define   MOUSE_X_SPEED              (0.5)
#define   MOUSE_Y_SPEED              (0.5)

/* Joystick behaviour */
//#define JOYSTICK_AXIS_RANGE          50

/* Serial */
#define     SERIAL_BAUD_RATE     115200  // Speed for USB serial console

float cal_value_x               = 10000.0; // ?
float cal_value_y               = 10000.0; // ?

#define   SCALE_TARE_TIME          2000  // The load cells need time before the first reading
#define   SAMPLES_TO_AVERAGE          1  // Must be a simple binary multiple (1, 2, 4, 8, 16, etc)
#define   JOYSTICK_INTERVAL          10  // ms between joystick position updates
#define   MOUSE_INTERVAL             10  // ms between mouse position updates

/* ----------------- Hardware-specific config ---------------------- */
/*
   The hardware config for this project depends on a variable set by the
   Arduino environment to detect the target board type. Currently only
   2 target boards are supported: Arduino Leonardo, and Seeeduino XIAO.

   Update the pin definitions in the section for your target board.

   This board detection method is also used in the program to load a
   different HID library and configure it differently depending on the
   board type. If using a Seeeduino XIAO, you must select Tools ->
   USB Stack -> TinyUSB.
*/

/**** Pins for Seeeduino XIAO ****/
#ifdef ARDUINO_SEEED_XIAO_M0
/* Load cell connections */
#define   LOADCELL_X_DOUT_PIN         0
#define   LOADCELL_X_SCK_PIN          1
#define   LOADCELL_Y_DOUT_PIN         2
#define   LOADCELL_Y_SCK_PIN          3

/* Inputs */
#define   TARE_BUTTON_PIN             6  // Pull this pin to GND to tare
#define   DISABLE_PIN                 7  // Pull this pin to GND to disable
#define   MOUSE_LEFT_BUTTON_PIN       8  // Pull this pin to GND for left click
#define   MOUSE_RIGHT_BUTTON_PIN      9  // Pull this pin to GND for right click
#endif
/**** End of XIAO pins ****/

/**** Pins for Arduino Leonardo ****/
#ifdef ARDUINO_AVR_LEONARDO
/* Load cell connections */
#define   LOADCELL_X_DOUT_PIN         4
#define   LOADCELL_X_SCK_PIN          5
#define   LOADCELL_Y_DOUT_PIN         6
#define   LOADCELL_Y_SCK_PIN          7

/* Inputs */
#define   TARE_BUTTON_PIN            A1  // Pull this pin to GND to tare
#define   DISABLE_PIN                 8  // Pull this pin to GND to disable
#define   MOUSE_LEFT_BUTTON_PIN      10
#define   MOUSE_RIGHT_BUTTON_PIN     11
#endif
/**** End of Leonardo pins ****/

/* I2C addresses */
#define   DIGIPOT_X_I2C_ADDR       0x28
#define   DIGIPOT_Y_I2C_ADDR       0x29

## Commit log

2018-02-06 Initial project import
    [ChairControlInterceptor.brd, ChairControlInterceptor.sch]
2018-02-06 Added Mini DIN-4 connector for Flysky trainer cable connection
    [ChairControlInterceptor.brd, ChairControlInterceptor.sch]
2018-02-07 Added second joystick input and changed outline to suit HB5922 case
    [ChairControlInterceptor.brd, ChairControlInterceptor.sch]
2018-02-07 Moved Arduino headers to correct location and adjusted connector positions
    [ChairControlInterceptor.brd, ChairControlInterceptor.sch]
2018-02-08 Routing and silkscreen
    [ChairControl.brd, ChairControl.sch]
2018-02-08 DRC and generated gerbers for v1.0 release
    [ChairControl.brd]
2018-03-03 Added trim inputs and extra headers for Mega footprint
    [ChairControl.brd, ChairControl.sch]
2018-03-27 Improved silkscreen
    [ChairControl.brd]
2018-07-10 Isolated 12V power from passthrough to allow separate power source
    [ChairControl.brd, ChairControl.sch]
2018-07-10 Forked project files for Mini version
    [ChairControlMini.brd, ChairControlMini.sch]
2018-07-10 Added CAN interface and removed second joystick input
    [ChairControlMini.brd, ChairControlMini.sch]
2018-07-12 Added power source selection and DRC for v1.0 release
    [ChairControlMini.brd, ChairControlMini.sch]
2018-07-18 Renamed project files to match SKU
    [CBMINI.brd, CBMINI.sch]
2018-07-23 Improved designators
    [CBMINI.brd]
2018-07-26 Added CAN bus interrupt connection to D2 for v1.1 release
    [CBMINI.brd, CBMINI.sch]
2018-07-27 Changed CAN crystal to 16MHz for compatibility with Arduino CAN shields
    [CBMINI.brd, CBMINI.sch]
2018-07-27 Added connector header board
    [CBMINICONN.brd, CBMINICONN.sch]
2019-04-11 Added extra input channels and CAN termination for v2.0 release
    [CBMINI.brd, CBMINI.sch]
2019-04-17 Improved value labels
    [CBMINI.brd]
2019-04-23 Changed input 5 to pin 5 for v2.1 release
    [CBMINI.brd, CBMINI.sch]
2019-06-18 Removed 120R termination, rotated connectors by 20 degrees, and added circular cut-out
    [CBMINICONN.brd, CBMINICONN.sch]
2019-08-30 Clearance for connectors
    [CBMINICONN.brd]
2019-11-13 Clickety click, replace replace
    [CBMINI.brd, CBMINI.sch]
2019-11-13 Restructured voltage regulators to support 24V CAN or Permobil controller for v2.2 release
    [CBMINI.brd, CBMINI.sch]
2019-12-05 File renaming
    [CBMINICONN.brd, CBMINICONN.sch, SB.brd, SB.sch]
2019-12-05 Basic schematic done and rough board outline
    [SB.brd, SB.sch]
2019-12-08 Replaced pot with rotary encoder, switched input and output sides
    [SB.brd, SB.sch]
2019-12-10 Big cleanup of routing and silkscreen, with updated 3D model for OLED
    [SB.brd, SB.sch]
2019-12-10 Replaced RJ10 socket with RJ12 and added haptic feedback output
    [SB.brd, SB.sch]
2019-12-10 Routing for haptic feedback
    [SB.brd]
2019-12-19 ERC / DRC for v1.0 release
    [SB.brd, SB.sch]
2019-12-19 Tweaks and cleanup, hopefully for v1.1 release
    [SB.brd, SB.sch]
2020-02-13 Added HX711 strain gauge amplifier directly on controller instead of external
    [SB.brd, SB.sch]
2020-02-13 Routing for v2.0 release
    [SB.brd, SB.sch]
2020-03-17 Synch with Fusion 360
    [SB.brd, SB.sch]
2020-04-30 Added mounting holes for v2.1 release
    [SB.brd, SB.sch]
2020-05-08 Added Tare button and beep stretch switch, still for v2.1 release
    [SB.brd, SB.sch]
2020-05-12 Removed haptic feedback and changed to RJ10 connector for v3.0 release
    [SB.brd, SB.sch]
2020-05-12 Still for v3.0 release: updated design rules and improved clearances
    [SB.brd, SB.sch]
2020-05-12 Added stencil DXF for v3.0
    [SB-tcream-v3_0.dxf]
2020-06-25 Renamed project files from SuperButton
    [SB-tcream-v3_0.dxf, ZEROSTICK.brd, ZEROSTICK.sch]
2020-07-06 Partical conversion from SB project
    [ZEROSTICK.brd, ZEROSTICK.sch]
2020-07-14 Moved hardware files into subdirectory
    [ZEROSTICK.brd, ZEROSTICK.sch]
2020-12-02 Added WIP PCB for load cell interface.
    [2LCI2C.brd, 2LCI2C.sch]
2020-12-08 New version of load cell interface with only 1 x NAU7802.
    [ZSLC.brd, ZSLC.sch]
2020-12-08 Partial conversion of early concept PCB.
    [2LCI2C.brd, 2LCI2C.sch]
2020-12-08 Added preview image of ZSLC PCB.
2021-02-01 Added images of previous and current prototype connections.
2021-03-29 Added ESP32 version of firmware.
2021-03-30 Matched schematic input channel labels to PCB silkscreen.
    [ZSLC.sch]
2021-03-30 Added firmware tests for ESP32 and NAU7802.
2021-04-06 Fixed labels and values on X and Y axis connectors.
    [ZSLC.brd, ZSLC.sch]
2021-04-09 Changed mouse button input pin assignments. Added debugging to show mouse button emulation mode.
2021-04-13 Apply scaling and range limiting to digipot outputs. Swap X and Y axis digipot I2C addresses to match CHAIRI2C board. Add separate debugging flags for different purposes.
2021-04-13 Added config option for digipot output speed. Added config option for full scale rating on load cells. Added config option for effort required for full scale deflection. Added config option for load 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

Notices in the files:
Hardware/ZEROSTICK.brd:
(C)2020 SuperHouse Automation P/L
